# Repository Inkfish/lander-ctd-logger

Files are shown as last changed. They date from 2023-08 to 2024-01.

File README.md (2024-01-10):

# CTD Logger for the Inkfish Open Oceans Landers

This repository holds firmware for the [SparkFun OpenLog][] specifically tailored to logging measurements from the [Sea-Bird SBE 49 FastCAT CTD][SBE 49] on the Inkfish Open Oceans landers.

  [SBE 49]: https://www.seabird.com/sbe-49-fastcat-ctd/product?id=60762467704
  [SparkFun OpenLog]: https://www.sparkfun.com/products/13712

The SBE 49 is capable of sampling at 16 Hz, but the lander controller functions best when it receives CTD data at 1 Hz. This firmware logs at the higher rate, then downsamples the data and passes it to the controller at the lower rate.

## Hardware

### Custom PCB

**(NEW):** The `hardware` directory contains KiCad designs for a printed circuit board that accepts a wider input voltage range and is designed to be significantly more resilient to power surges.

### Breadboard

The only components needed are the [SparkFun OpenLog][] and a [MAX3232 transceiver breakout][MAX3232].



(Note that some components are represented as SIP ICs for purposes of illustration. The leftmost pin of the MAX3232 transceiver above is `T1OUT`.)

In summary, the circuit interposes the communication between the CTD and Lander Control Board:

    +-------+          +---------------+         +-----------+
    | CTD   |          | MAX3232       |         | OpenLog   |
    |       |          |               |         |           |
    |   TX -------------> R1IN  R1OUT ------------> RX       |
    |       |  RS-232  |               |   TTL   |           |
    |       |    +------- T1OUT  T1IN <------------ TX       |
    |       |    |     |               |         |           |
    +-------+    |     +---------------+         +-----------+
                 |
                 |     +-------------------------------------+
                 |     | LCB                                 |
                 |     |                                     |
                 +------> CTD_RX                             |
                       |                                     |
                       +-------------------------------------+

**Note:** Consider the need to attach the programmer to the OpenLog. See Programming section below.

  [MAX3232]: https://www.sparkfun.com/products/11189

## Compiling

This project uses [PlatformIO][]. You can build the firmware and program the OpenLog using the PlatformIO Core CLI tool.

  [PlatformIO]: https://platformio.org/

First, clone the repository with submodules:

    git submodule update --init

Patch `SerialPort.h` to disable `BUFFERED_TX` and `ENABLE_RX_ERROR_CHECKING`:

    sed -i.bak \
      -e 's/\(#define BUFFERED_TX\) 1/\1 0/' \
      -e 's/\(#define ENABLE_RX_ERROR_CHECKING\) 1/\1 0/' \
      Libraries/SerialPort/SerialPort/SerialPort.h

Compile the project using PlatformIO to check for errors:

    pio run

## Programming

The OpenLog can be programmed using a 4-wire TTL UART to USB adapter. Review the [OpenLog Hookup Guide][hookup] for details on wiring. Importantly, the OpenLog `DTR` pin (inexplicably labeled `GRN`) must be connected to the programmer's `DTR` or `RTS` output.

  [hookup]: https://learn.sparkfun.com/tutorials/openlog-hookup-guide#hardware-hookup

    pio run -t upload

### Programming with a RS-232 cable

A USB to RS-232 cable (DB-9 connector) can also be used for programming. The `RX`/`TX` pinout on the DB-9 connector must be confirmed due to the various permutations.

  | DB-9              | MAX3232           | OpenLog |
  | ----------------- | ----------------- | ------- |
  | `TX` (pin 2 or 3) | `R1IN` → `R1OUT`  | `RX`    |
  | `RX` (pin 2 or 3) | `T1OUT` ← `T1IN`  | `TX`    |
  | `DTR` (pin 4)     | `R2IN`  → `R2OUT` | `GRN`   |
  | `GND` (pin 5)     | `GND`             | `GND`   |

### Programming with a Bus Pirate

The [Bus Pirate][] can be used as a programmer. Attach the pins as follows:

  | Bus Pirate | OpenLog |
  | ---------- | ------- |
  | `MOSI`     | `RX`    |
  | `MISO`     | `TX`    |
  | `CLK`      | `GRN`   | 
  | `GND`      | `GND`   |

Place the Bus Pirate into the transparent UART bridge mode with flow control signaling:

    # Enter UART mode, use baud 115200 for programming
    HiZ>m
    2. UART
    (1)>2
    ...

    # Enable power output on the pins
    UART>W
    POWER SUPPLIES ON
    Clutch engaged!!!

    # Start the transparent bridge
    UART>(3)
    UART bridge
    Reset to exit
    Are you sure? y

Disconnect the terminal session and proceed with programming the board.

  [Bus Pirate]: http://dangerousprototypes.com/docs/Bus_Pirate

## Configuration

By default, the OpenLog expects to receive and transmit data at 9600 baud, the same rate as the Lander Control Board. If this needs to be changed, a different baud rate can be written to the file `config.txt` at the root of the microSD card.

The SBE 49 must be configured for `OUTPUTFORMAT=3`, engineering units in decimal. 

## Testing

A quick and dirty test script can be used to send fake samples to the logger from a PC. The script counts the number of downsampled replies that match expected values.

    python3 test/simctd.py --sal --sv /dev/tty.usbserial

The `--sal` and `--sv` flags simulate the `OUTPUTSAL` (salinity) and `OUTPUTSV` (sound velocity) options on the SBE 49.

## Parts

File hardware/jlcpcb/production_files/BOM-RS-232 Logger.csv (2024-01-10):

Comment | Designator | Footprint | LCSC
1 uF | C1 | C_0805_2012Metric | C2798196
Conn_01x06 | J1 | PinSocket_1x06_P2.54mm_Vertical | C2897443
SW_DIP_x02 | SW1 | SW_DIP_SPSTx02_Slide_6.7x6.64mm_W8.61mm_P2.54mm_LowProfile | C314502
47Ω | R1,R2,R3 | R_0603_1608Metric | C319576
Conn_01x05 | J2 | TerminalBlock_Phoenix_PT-1,5-5-3.5-H_1x05_P3.50mm_Horizontal | C3646874
D | D1 | DO-214BA_MCH | C3757764
Conn_01x06 | J3 | PinHeader_1x06_P2.54mm_Vertical | C6332199
SMBJ5.0CA | D2,D3,D4 | D_SMA | C83324
10 uF | C5,C7,C9 | CAP_4 X 5.8_PAN | C84356
MAX3232E | U1 | 21-0056-E_90-0106-16L_MXM | C86262
0.1 uF | C6,C8 | C_0805_2012Metric | C913936
TLV70433DBVR | U2 | DBV0005A_N | C94917
4.7 uF | C2,C3,C4 | C_0805_2012Metric | C98192

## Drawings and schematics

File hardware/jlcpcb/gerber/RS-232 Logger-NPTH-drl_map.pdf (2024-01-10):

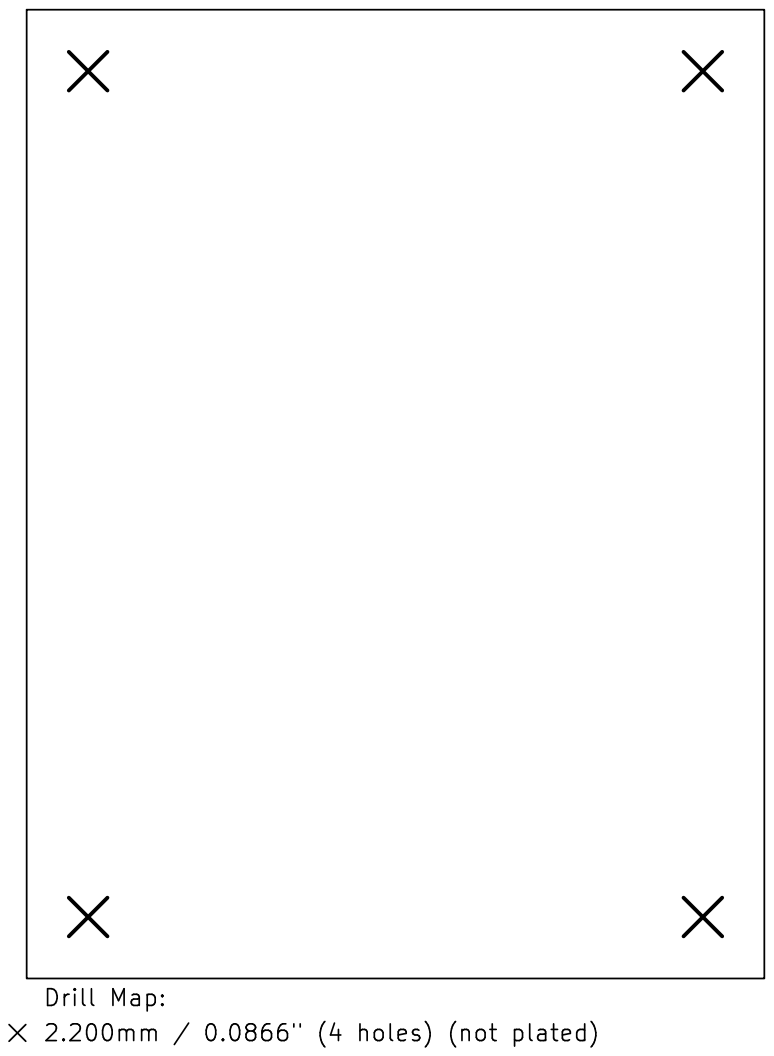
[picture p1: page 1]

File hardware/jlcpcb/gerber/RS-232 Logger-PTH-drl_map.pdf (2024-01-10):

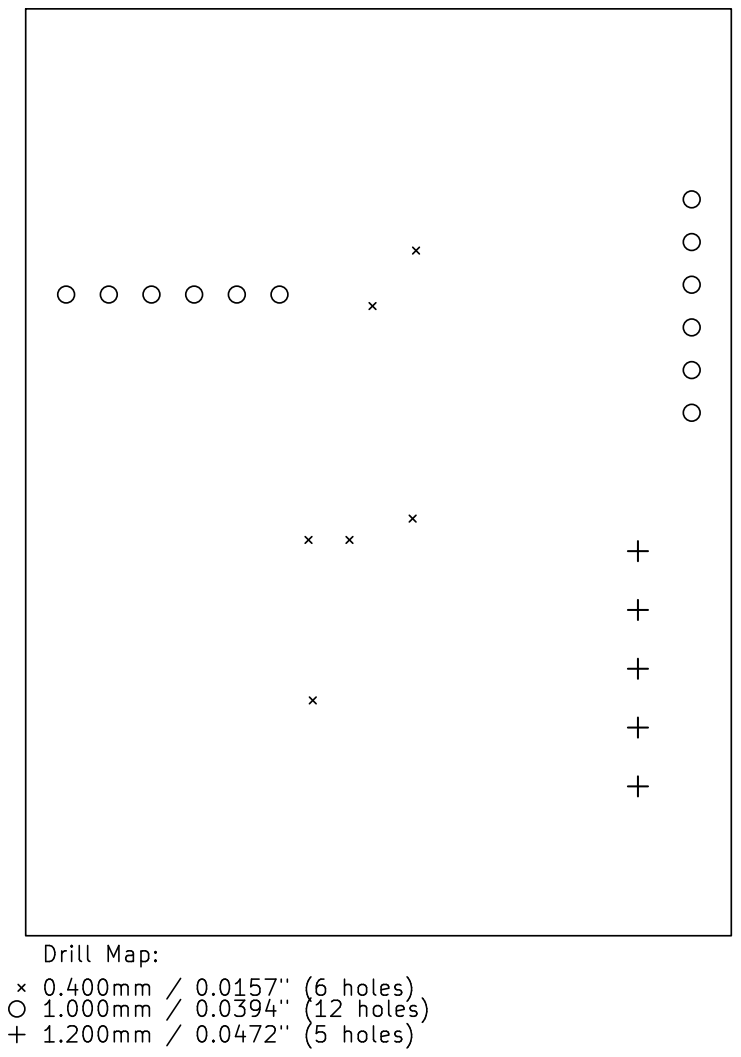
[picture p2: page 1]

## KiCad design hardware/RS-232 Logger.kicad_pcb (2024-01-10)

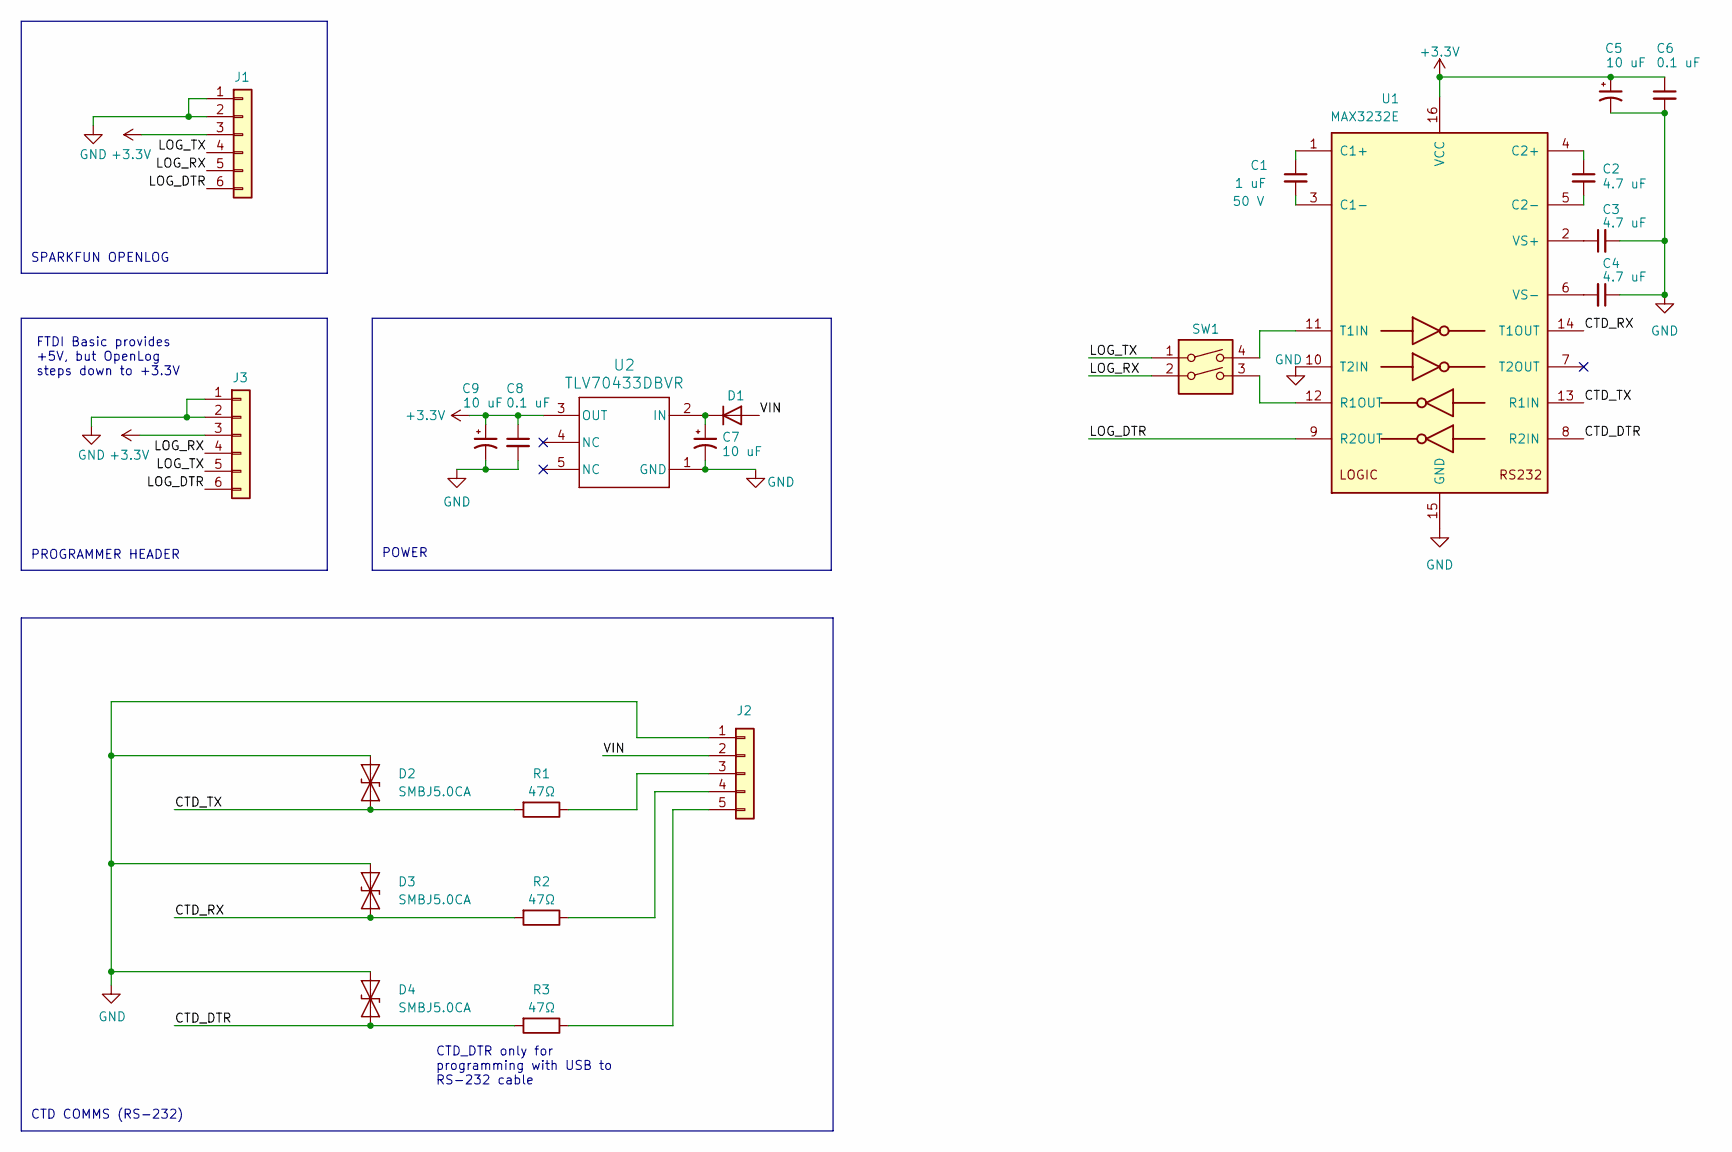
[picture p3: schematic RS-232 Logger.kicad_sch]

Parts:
C1: 1 uF; C_0805_2012Metric; Voltage 50 V; DigiKey CL21B105KBFNNNG
C2, C3, C4: 4.7 uF; C_0805_2012Metric; DigiKey CL21A475KBQNNNE
C5, C9: 10 uF; CAP_4 X 5.8_PAN; DigiKey EEE-FK1C100R
C6, C8: 0.1 uF; C_0805_2012Metric; DigiKey CL21B104KBCNNNC
C7: 10 uF; CAP_4 X 5.8_PAN
D1: D; DO-214BA_MCH
D2, D3, D4: SMBJ5.0CA; D_SMA
J1: Conn_01x06; PinSocket_1x06_P2.54mm_Vertical
J2: Conn_01x05; TerminalBlock_Phoenix_PT-1,5-5-3.5-H_1x05_P3.50mm_Horizontal
J3: Conn_01x06; PinHeader_1x06_P2.54mm_Vertical
R1, R2, R3: 47Ω; R_0603_1608Metric; DigiKey ESR03EZPJ470
SW1: SW_DIP_x02; SW_DIP_SPSTx02_Slide_6.7x6.64mm_W8.61mm_P2.54mm_LowProfile
U1: MAX3232E; 21-0056-E_90-0106-16L_MXM
U2: TLV70433DBVR; DBV0005A_N

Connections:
+3.3V: C5.1, C6.1, C8.1, C9.1, J1.3, J3.3, U1.16 (VCC), U2.3 (OUT)
/CTD_DTR: D4.2 (A2), R3.2, U1.8 (R2IN)
/CTD_RX: D3.2 (A2), R2.2, U1.14 (T1OUT)
/CTD_TX: D2.2 (A2), R1.2, U1.13 (R1IN)
/LOG_DTR: J1.6, J3.6, U1.9 (R2OUT)
/LOG_RX: J1.5, J3.4, SW1.2
/LOG_TX: J1.4, J3.5, SW1.1
/VIN: D1.2 (A), J2.2
GND: C3.2, C4.1, C5.2, C6.2, C7.2, C8.2, C9.2, D2.1 (A1), D3.1 (A1), D4.1 (A1), J1.1, J1.2, J2.1, J3.1, J3.2, U1.10 (T2IN), U1.15 (GND), U2.1 (GND)
unnamed: C7.1, D1.1 (K), U2.2 (IN)
unnamed: J2.3, R1.1
unnamed: J2.4, R2.1
unnamed: J2.5, R3.1
unnamed: C1.1, U1.1 (C1+)
unnamed: C1.2, U1.3 (C1-)
unnamed: C2.1, U1.4 (C2+)
unnamed: C2.2, U1.5 (C2-)
unnamed: SW1.3, U1.12 (R1OUT)
unnamed: SW1.4, U1.11 (T1IN)
unnamed: C3.1, U1.2 (VS+)
unnamed: C4.2, U1.6 (VS-)

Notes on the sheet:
CTD_DTR only for programming with USB to RS-232 cable
FTDI Basic provides +5V, but OpenLog steps down to +3.3V
CTD COMMS (RS-232)
SPARKFUN OPENLOG
POWER
PROGRAMMER HEADER

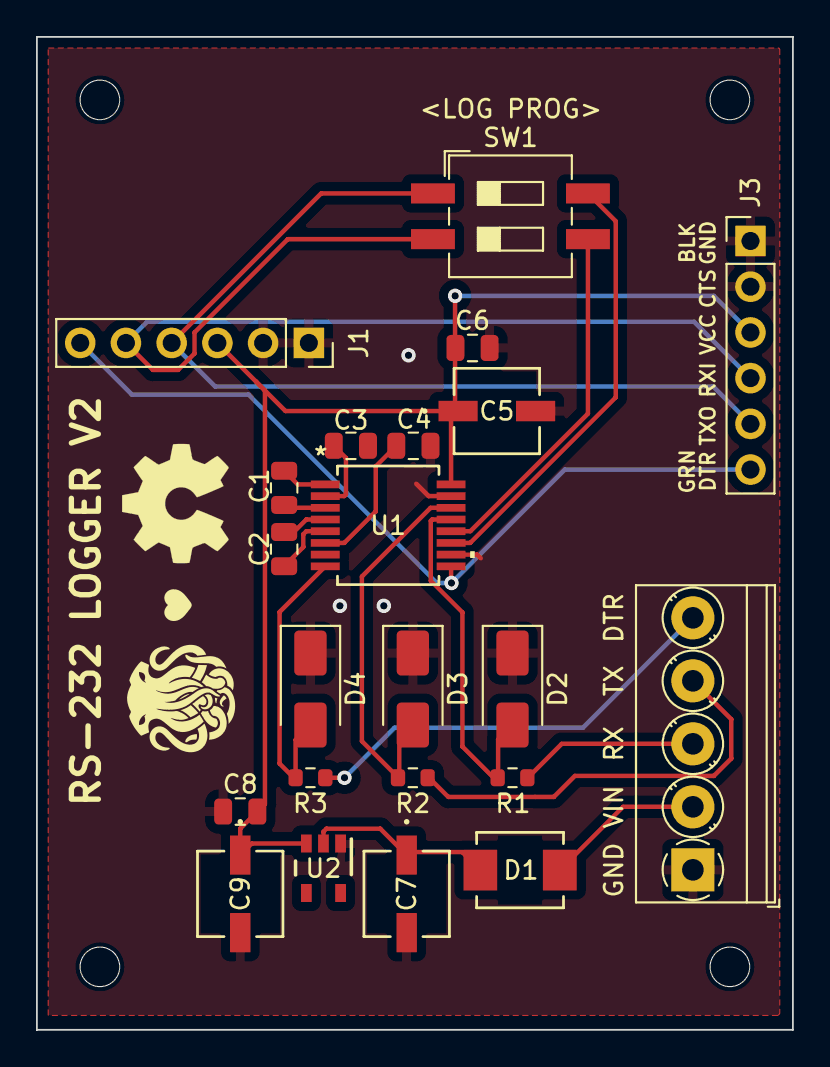
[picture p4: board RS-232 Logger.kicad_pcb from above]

Board: 2 copper layers, 42.0 x 55.2 mm, 22 parts (0 on the bottom side), 21 nets.

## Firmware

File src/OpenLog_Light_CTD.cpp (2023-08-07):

/*
 12-3-09
 Nathan Seidle
 SparkFun Electronics
 
 OpenLog hardware and firmware are released under the Creative Commons Share Alike v3.0 license.
 http://creativecommons.org/licenses/by-sa/3.0/
 Feel free to use, distribute, and sell varients of OpenLog. All we ask is that you include attribution of 'Based on OpenLog by SparkFun'.
 
 OpenLog is a simple serial logger based on the ATmega328 running at 16MHz. The ATmega328
 is able to talk to high capacity (larger than 2GB) SD cards. The whole purpose of this
 logger was to create a logger that just powered up and worked. OpenLog ships with an Arduino/Optiboot 
 115200bps serial bootloader running at 16MHz so you can load new firmware with a simple serial
 connection.
 
 This version has the command line interface stripped out in order to simplify the overall program and increase 
 the receive buffer (RAM). You can still configure some of the options via the config.txt file.

 For even faster logging, see OpenLog_Minimal.
 
 */
#define __PROG_TYPES_COMPAT__ //Needed to get SerialPort.h to work in Arduino 1.6.x

#include <Arduino.h>

#include <SPI.h>
#include <SdFat.h> //We do not use the built-in SD.h file because it calls Serial.print
#include <SerialPort.h> //This is a new/beta library written by Bill Greiman. You rock Bill!
#include <EEPROM.h>
#include <FreeStack.h> //Allows us to print the available stack/RAM size

#include "CTD.h"

SerialPort<0, 512, 0> NewSerial;
//This is a very important buffer declaration. This sets the <port #, rx size, tx size>. We set
//the TX buffer to zero because we will be spending most of our time needing to buffer the incoming (RX) characters.

#include <avr/sleep.h> //Needed for sleep_mode
#include <avr/power.h> //Needed for powering down perihperals such as the ADC/TWI and Timers

#define SD_CHIP_SELECT 10 //On OpenLog this is pin 10

//Debug turns on (1) or off (0) a bunch of verbose debug statements. Normally use (0)
//#define DEBUG  1
#define DEBUG  0

//The bigger the receive buffer, the less likely we are to drop characters at high speed. However, the ATmega has a limited amount of
//RAM. This debug mode allows us to view available RAM at various stages of the program
//#define RAM_TESTING  1 //On
#define RAM_TESTING  0 //Off

#define CFG_FILENAME "config.txt" //This is the name of the file that contains the unit settings

#define MAX_CFG "115200" //= 115200 bps
#define CFG_LENGTH (strlen(MAX_CFG) + 1) //Length of text found in config file

//Internal EEPROM locations for the user settings
#define LOCATION_BAUD_SETTING		0x01
#define LOCATION_FILE_NUMBER_LSB	0x03
#define LOCATION_FILE_NUMBER_MSB	0x04
#define LOCATION_BAUD_SETTING_HIGH	0x09
#define LOCATION_BAUD_SETTING_MID	0x0A
#define LOCATION_BAUD_SETTING_LOW	0x0B

#define BAUD_MIN  300
#define BAUD_DEFAULT 9600
#define BAUD_MAX  1000000

//STAT1 is a general LED and indicates serial traffic
#define STAT1  5 //On PORTD
#define STAT1_PORT  PORTD
#define STAT2  5 //On PORTB
#define STAT2_PORT  PORTB
const byte statled1 = 5;  //This is the normal status LED
const byte statled2 = 13; //This is the SPI LED, indicating SD traffic

//Blinking LED error codes
#define ERROR_SD_INIT	  3
#define ERROR_NEW_BAUD	  5
#define ERROR_CARD_INIT   6
#define ERROR_VOLUME_INIT 7
#define ERROR_ROOT_INIT   8
#define ERROR_FILE_OPEN   9

#define OFF   0x00
#define ON    0x01

SdFat sd;

long setting_uart_speed; //This is the baud rate that the system runs at

//Forward declarations
void serial_out(const char* str);
void systemError(byte error_type);
char* newlog(void);
byte append_file(char* file_name);
void blink_error(byte ERROR_TYPE);
void read_system_settings(void);
void read_config_file(void);
void record_config_file(void);
void writeBaud(long uartRate);
long readBaud(void);


//Wrapper around NewSerial::write() that can be passed to the CTD handler.
void serial_out(const char* str) {
  NewSerial.write(str);
}


//Handle errors by printing the error type and blinking LEDs in certain way
//The function will never exit - it loops forever inside blink_error
void systemError(byte error_type)
{
  //NewSerial.print(F("Error "));
  switch(error_type)
  {
  case ERROR_CARD_INIT:
    //NewSerial.print(F("card.init")); 
    blink_error(ERROR_SD_INIT);
    break;
  case ERROR_VOLUME_INIT:
    //NewSerial.print(F("volume.init")); 
    blink_error(ERROR_SD_INIT);
    break;
  case ERROR_ROOT_INIT:
    //NewSerial.print(F("root.init")); 
    blink_error(ERROR_SD_INIT);
    break;
  case ERROR_FILE_OPEN:
    //NewSerial.print(F("file.open")); 
    blink_error(ERROR_SD_INIT);
    break;
  }
}

void setup(void)
{
  pinMode(statled1, OUTPUT);

  //Power down various bits of hardware to lower power usage  
  set_sleep_mode(SLEEP_MODE_IDLE);
  sleep_enable();

  //Shut off TWI, Timer2, Timer1, ADC
  ADCSRA &= ~(1<<ADEN); //Disable ADC
  ACSR = (1<<ACD); //Disable the analog comparator
  DIDR0 = 0x3F; //Disable digital input buffers on all ADC0-ADC5 pins
  DIDR1 = (1<<AIN1D)|(1<<AIN0D); //Disable digital input buffer on AIN1/0

  power_twi_disable();
  power_timer1_disable();
  power_timer2_disable();
  power_adc_disable();

  read_system_settings(); //Load all system settings from EEPROM

  //NewSerial.print(F("1"));

  //Setup SD & FAT
  if (!sd.begin(SD_CHIP_SELECT, SPI_FULL_SPEED)) systemError(ERROR_CARD_INIT);
  if (!sd.chdir()) systemError(ERROR_ROOT_INIT); //Change to root directory. All new file creation will be in root.

  //NewSerial.print(F("2"));

  //Search for a config file and load any settings found. This will over-ride previous EEPROM settings if found.
  read_config_file();

  //Setup UART
  NewSerial.begin(setting_uart_speed);
  if (setting_uart_speed < 500)      // check for slow baud rates
  {
    //There is an error in the Serial library for lower than 500bps.
    //This fixes it. See issue 163: https://github.com/sparkfun/OpenLog/issues/163
    // redo USART baud rate configuration
    UBRR0 = (F_CPU / (16UL * setting_uart_speed)) - 1;
    UCSR0A &= ~_BV(U2X0);
  }
}

void loop(void)
{
  append_file(newlog()); //Append the file name that newlog() returns
  while(1); //We should never get this far
}

//Log to a new file everytime the system boots
//Checks the spots in EEPROM for the next available LOG# file name
//Updates EEPROM and then appends to the new log file.
//Limited to 65535 files but this should not always be the case.
char* newlog(void)
{
  byte msb, lsb;
  uint16_t new_file_number;

  SdFile newFile; //This will contain the file for SD writing

  //Combine two 8-bit EEPROM spots into one 16-bit number
  lsb = EEPROM.read(LOCATION_FILE_NUMBER_LSB);
  msb = EEPROM.read(LOCATION_FILE_NUMBER_MSB);

  new_file_number = msb;
  new_file_number = new_file_number << 8;
  new_file_number |= lsb;

  //If both EEPROM spots are 255 (0xFF), that means they are un-initialized (first time OpenLog has been turned on)
  //Let's init them both to 0
  if((lsb == 255) && (msb == 255))
  {
    new_file_number = 0; //By default, unit will start at file number zero
    EEPROM.write(LOCATION_FILE_NUMBER_LSB, 0x00);
    EEPROM.write(LOCATION_FILE_NUMBER_MSB, 0x00);
  }

  //The above code looks like it will forever loop if we ever create 65535 logs
  //Let's quit if we ever get to 65534
  //65534 logs is quite possible if you have a system with lots of power on/off cycles
  if(new_file_number == 65534)
  {
    //Gracefully drop out to command prompt with some error
    //NewSerial.print(F("!Too many logs:1!"));
    return(0); //Bail!
  }

  //If we made it this far, everything looks good - let's start testing to see if our file number is the next available

  //Search for next available log spot
  //char new_file_name[] = "LOG00000.TXT";
  static char new_file_name[13];
  while(1)
  {
    sprintf_P(new_file_name, PSTR("LOG%05d.TXT"), new_file_number); //Splice the new file number into this file name

    //Try to open file, if fail (file doesn't exist), then break
    if (newFile.open(new_file_name, O_CREAT | O_EXCL | O_WRITE)) break;

    //Try to open file and see if it is empty. If so, use it.
    if (newFile.open(new_file_name, O_READ)) 
    {
      if (newFile.fileSize() == 0)
      {
        newFile.close();        // Close this existing file we just opened.
        return(new_file_name);  // Use existing empty file.
      }
      newFile.close(); // Close this existing file we just opened.
    }

    //Try the next number
    new_file_number++;
    if(new_file_number > 65533) //There is a max of 65534 logs
    {
      //NewSerial.print(F("!Too many logs:2!"));
      return(0); //Bail!
    }
  }
  newFile.close(); //Close this new file we just opened

  new_file_number++; //Increment so the next power up uses the next file #

  //Record new_file number to EEPROM
  lsb = (byte)(new_file_number & 0x00FF);
  msb = (byte)((new_file_number & 0xFF00) >> 8);

  EEPROM.write(LOCATION_FILE_NUMBER_LSB, lsb); // LSB

  if (EEPROM.read(LOCATION_FILE_NUMBER_MSB) != msb)
    EEPROM.write(LOCATION_FILE_NUMBER_MSB, msb); // MSB

#if DEBUG
  //NewSerial.print(F("\nCreated new file: "));
  //NewSerial.println(new_file_name);
#endif

  //  append_file(new_file_name);
  return(new_file_name);
}

//This is the most important function of the device. These loops have been tweaked as much as possible.
//Modifying this loop may negatively affect how well the device can record at high baud rates.
//Appends a stream of serial data to a given file
//Assumes the currentDirectory variable has been set before entering the routine
//Returns 0 on error
//Returns 1 on success
byte append_file(char* file_name)
{
  SdFile workingFile;

  // O_CREAT - create the file if it does not exist
  // O_APPEND - seek to the end of the file prior to each write
  // O_WRITE - open for write
  if (!workingFile.open(file_name, O_CREAT | O_APPEND | O_WRITE)) systemError(ERROR_FILE_OPEN);

  if (workingFile.fileSize() == 0) {
    //This is a trick to make sure first cluster is allocated - found in Bill's example/beta code
    workingFile.rewind();
    workingFile.sync();
  }

  //This is the 2nd buffer. It pulls from the larger Serial buffer as quickly as possible.
  //The built-in Arduino serial buffer is 64 bytes: https://www.arduino.cc/en/Serial/Available
  const byte LOCAL_BUFF_SIZE = 128;
  byte localBuffer[LOCAL_BUFF_SIZE];

  const unsigned int MAX_IDLE_TIME_MSEC = 500; //The number of milliseconds before unit goes to sleep
  unsigned long lastSyncTime = millis(); //Keeps track of the last time the file was synced
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

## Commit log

2023-07-30 Remove unnecessary files
    [OpenLog.brd, OpenLog.sch, OpenLog_Panel_v15.brd]
2023-08-06 Silence debug output on TX pin
2023-08-07 Initial README
    [CTD logger.fzz]
2023-08-07 Add more wiring information
2023-08-07 Tweak wires to improve clarity
    [CTD logger.fzz]
2023-08-07 Use dtostrf to build the output string
    Apparently Arduino's printf() cannot handle %f specifiers.
2023-08-13 Fix label on schematic
    [CTD logger.fzz]
2024-01-10 Use 3.3V power input
    The OpenLog features a voltage regulator that steps input power down to 3.3V.
    According to the ATmega328P data sheet (section 28, Electrical Characteristics),
    the maximum voltage on any pin is VCC + 0.5 = 3.8V.
    The SP3232E transceiver's voltage level on RxOUT = VCC + 0.3. Therefore the
    transceiver's VCC cannot exceed 3.5V or it will be out of spec with the ATmega.
    [CTD logger.fzz]
2024-01-10 Update diagram with new Fritzing part
    [CTD logger.fzz]
2024-01-10 Add RS-232 Logger PCB design files
    [BOM-RS-232 Logger.csv, CPL-RS-232 Logger.csv, RS-232 Logger-CuBottom.gbr, RS-232 Logger-CuTop.gbr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]
